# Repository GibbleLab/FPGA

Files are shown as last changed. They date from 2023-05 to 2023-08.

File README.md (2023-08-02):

# Many-Channel FPGA Control System

Authors:
Daniel Schussheim and Kurt Gibble (GibbleLab@psu.edu)

Department of Physics

The Pennsylvania State University

This FPGA system is a general-purpose control system with fast and slow analog inputs and outputs and digital inputs and outputs. The baseline configuration implements 9 PID servos with MHz bandwidths and 8 low bandwidth servos, generates 3 arbitrary waveform outputs, and has modulation, lock-in detection, and digital signal processing.  It was developed to frequency stabilize lasers and frequency doubling and summing cavities, stabilize temperatures, and perform a number of controls and signal processing for a cadmium laser-cooling experiment. The developed hardware and firmware for the inputs and outputs can be used for a variety of applications, connecting the system’s inputs and outputs to the provided or user-developed software filters.

The system uses an Enclustra Mercury+ KX2 FPGA module that plugs into a custom baseboard. The Xilinx FPGA is a XC7K160T-2FFG676I, which has 25,350 logic slices, 600 DSP slices and 325 36 kb RAM blocks. Our baseline FPGA software uses 88,576 look up tables distributed over nearly all, 25,196, of the logic slices. Other pin-compatible FPGA modules with more resources are available. The baseboard was designed with Altium Designer Version 21.3.2 (Build 30), and the power supply board was designed in CircuitMaker.

This work builds on a system developed by [NIST](https://github.com/nist-ionstorage/digital-servo), adding more I/O channels, using a larger FPGA, and simplifying filters to allow more servos on a single FPGA. The software is written in Verilog and the bitstreams were generated with Vivado 2020.1.

The supporting files for this many-channel FPGA system (MCFS) are:

* __manual.pdf__: User guide describing the firmware and software, hardware, and assembly of this MCFS.
* __Mercury_AD_Baseboard__: Altium project with the baseboard design files, gerber and drill files (gerber-drill.rar) for printing, and the bill-of-materials (BOM.xlsx) for assembly.
* __Power_Supply__: The power supply board schematics, board layout, gerber and drill files, and bill-of-materials.
* __MCFS_HD__: Vivado Hierarchical Design Project with the Verilog HDL firmware and software and Tcl scripts for generating bitstreams.
* __Serial-parameter-input__: Spreadsheets to adjust the fast and slow servo gains and roll-off frequencies, arbitrary waveform parameters, and to test the fast DAC’s. A Labview program and its executable file are also included.
* __Vivado GUI Projects__: This [page](https://sites.psu.edu/gibble/fpga_gui) has Vivado GUI projects with simplified PID filters that retain 25% gain resolution with combinations of omitting the LSB rounding of the filter cutoff frequencies or have 2<sup>n</sup> resolution on cutoff frequencies for the proportional or integral filters, or 2<sup>n/2</sup> resolution for the differential rolloff with a damping resolution of 2<sup>n</sup>. These allow timing margin in the full project at 100 MS/s sample rates.

## Schematic of the baseline MCFS software configuration.

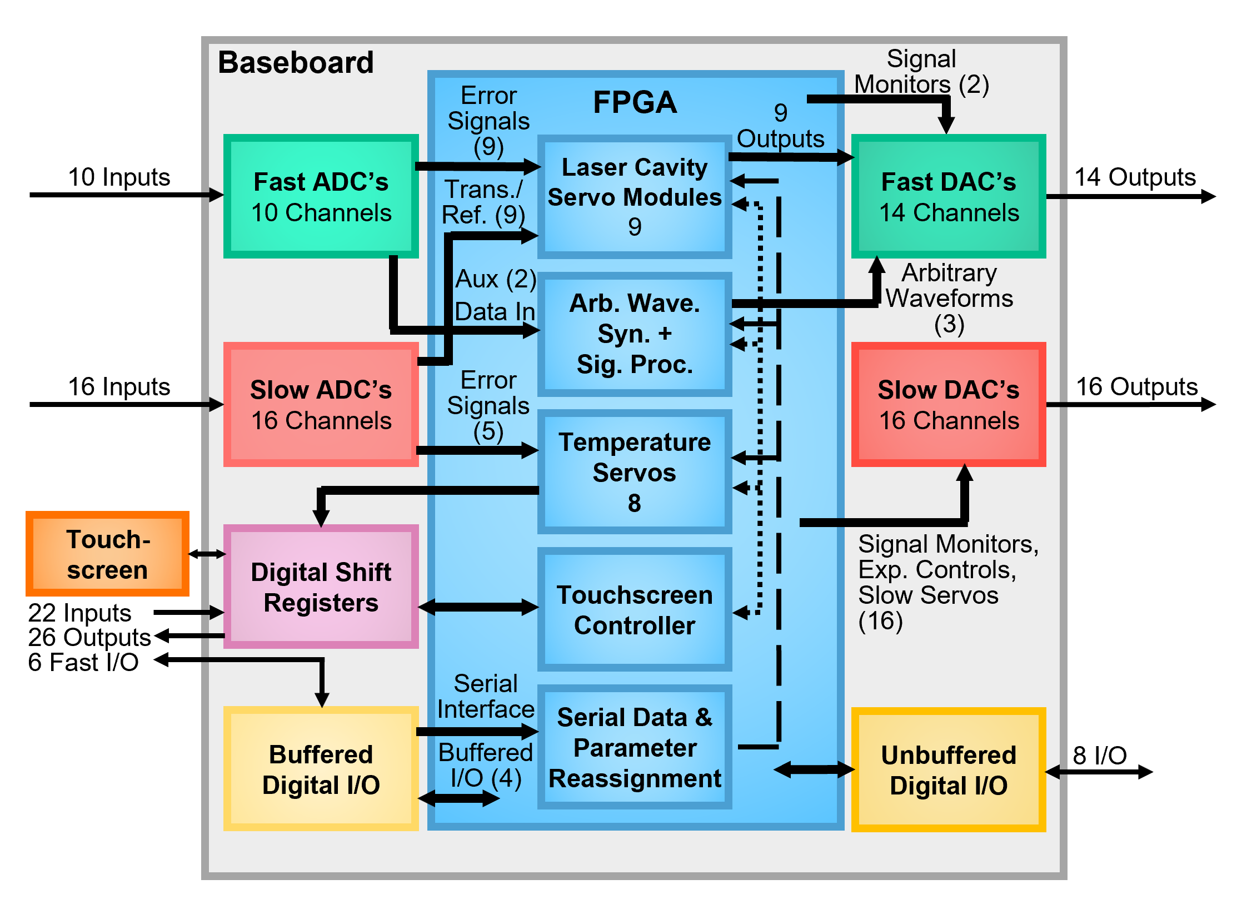
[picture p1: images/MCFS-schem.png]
Schematic


## Summary of inputs and outputs

| I/O Type              |      | # of Channels | Sample Rate (MS/s) | Range (V) |
| :---                  | :--- | :---         | :---               | :---      |
| Fast ADC (LTC2194)    | IN   | 10            | 100                | &#xB1;4   |
| Fast DAC (MAX5875)    | OUT  | 14            | 100                | &#xB1;18  |
| Slow ADC (LTC2335-16) | IN   | 16            | Maximum sample rate is 1 channel every &#x3BC;s on each of 2 chips, e.g., 2 ch. @ 1 MS/s or 16 ch. @ 125 kS/s | &#xB1;10 |
| Slow DAC (LTC2666-16) | OUT  | 16 | 0.05 | &#xB1;18  |
| Fast Digital I/O, buffered (TXS0108E-Q1) | IN/OUT | 6             | 100       | 5V digital |
| Fast Digital I/O, unbuffered (FPC connector) | IN/OUT | 8         | 100+      | 3.3V digital |
| Slow Digital In (74LV165A)  | IN  | 22 | 2 | 3.3V digital |
| Slow Digital Out (74VHC595) | OUT | 26 | 19 ch. @ 2 MS/s, 7 ch. @ 3 MS/s | 3.3V digital |
| Display connectors (DB9)| N/A | 2 | N/A | N/A |

## Additional Information

A paper describing the IIR PID filters, enhanced Hänsch-Couillaud laser locks with slow offset corrections, variable duty cycle temperature servos, and more information about the system is available at:
"[A many-channel FPGA control system](https://doi.org/10.1063/5.0157330)," Daniel T. Schussheim & Kurt Gibble, Rev Sci Instrum <b>94</b>, 085101 (2023); [arXiv:2307.16008](https://arxiv.org/abs/2307.16008).

## Acknowledgements

Financial support to develop this project from the National Science Foundation is gratefully acknowledged.

## License

This work is licensed under a [Creative Commons Attribution-NonCommercial-ShareAlike 3.0 Unported License](https://creativecommons.org/licenses/by-nc-sa/3.0/).

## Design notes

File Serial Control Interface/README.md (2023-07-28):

# Serial Control Interface

The FPGA firmware module serialLine.v uses a two-wire 100 kS/s serial interface to set servo and arbitrary waveform parameters. The serial packet begins and ends with a 16-bit handshake that specifies the parameters to update, which are encoded as 27 sequential 35-bit numbers. 

The gains and other servo parameters, or arbitrary waveform parameters, can be entered into the spreadsheets in this folder. Spreadsheet macros, with keyboard shortcut Ctrl-q, generate the serial packets, writes them to a file param.txt, and calculates the PID transfer function, which is displayed.

The LabVIEW vi Write SRS Arb.vi loads PIDparam.txt as a “point” arbitrary waveform on an SRS DS345 via GPIB. Write SRS Arb.exe is also provided, which requires the 64-bit 2023.Q1 LabVIEW Run-Time Engine. A driver for the GPIB interface may be required; if using the NI GPIB-USB-HS adapter, the 2022 Q4 NI-488.2 driver and NI-488.2 Runtime are needed. For the default firmware, the SRS output should be connected to FPGA pin C12 (serial_in in top.sv) and the SRS trigger output to A14 (serial_trig_in in top.sv). The SRS should be configured for an arbitrary waveform output, with an internal trigger (4 Hz), 100 kHz sample rate, and a 3.2V pk-to-pk amplitude with 0 offset.

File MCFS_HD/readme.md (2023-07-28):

See the manual for the procedure to generate a new bitstream with Vivado HD FLow. The first step is to run Tcl_Script_Generator.tcl, with “source Tcl_Script_Generator.tcl –notrace” in the Vivado 2020.1 Tcl Shell, and then “source MakeBitstream.tcl -notrace”. The design checkpoints, *.dcp, in the Implement and Synth subdirectories /top are for the bitstream, top.bit, which was extensively tested. With 25% resolution on the fast PID rolloff frequencies, it does not have timing margin but nonetheless no operational errors were observed in testing. Some modules have had subsequent minor revisions that are not included in those files. These [GUI Flow projects](https://sites.psu.edu/gibble/fpga_gui), with simplified filter rolloffs, have timing margin.

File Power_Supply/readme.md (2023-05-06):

This is the design for a separate power supply board that uses a single 15 V input to generate the various voltages needed by the baseboard. The source files are available in the CircuitMaker Repository: https://bit.ly/3VuMqpN.

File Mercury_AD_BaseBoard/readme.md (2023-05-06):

Schematic, bill of materials, Gerber and Altium files for the baseboard.

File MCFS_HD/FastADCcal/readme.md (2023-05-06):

See the manual for the procedure to generate bitstreams for Fast ADC testing. After executing Tcl_Script_Generator.tcl in the MCFS_HD directory, the multiphase.tcl and multitap.tcl scripts execute design.tcl multiple times, saving files, including bitstreams and debugging probes files, for each run in Implement\BIT\dump. These are executed in the Vivado 2020.1 Tcl Shell with “source FastADCcal/multiphase.tcl -notrace” and “source FastADCcal/multitap.tcl -notrace”.

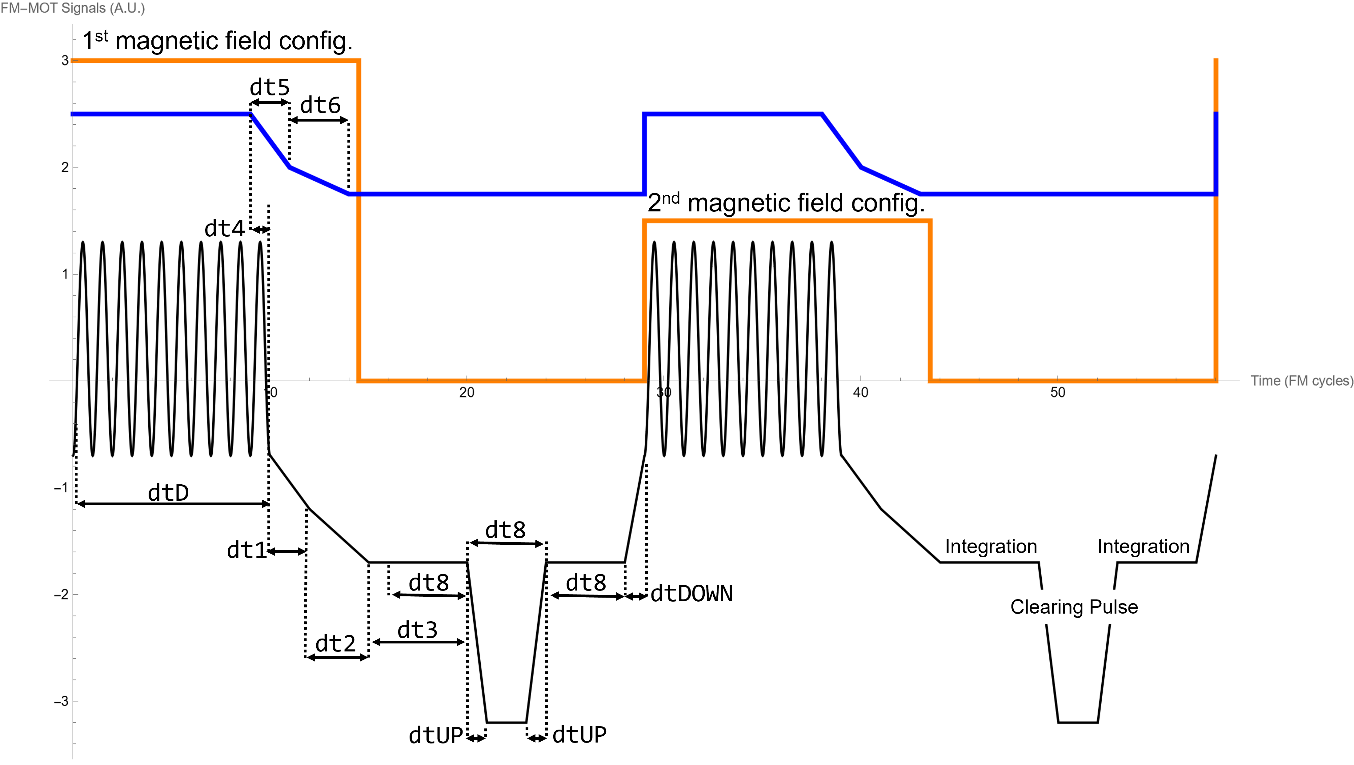
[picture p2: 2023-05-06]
Serial Control Interface/FM-MOT Arbitrary Waveform Definitions.png

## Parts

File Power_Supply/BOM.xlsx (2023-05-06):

Comment | Description | Designator | Quantity
4.7 uF (1210) | CAP CER 4.7UF 50V 10% X7R 1210 | C000, C001, C100, C110, C120, C130, C140, C400 | 8
 | CAP CER 330PF 50V 10% X7R 0603 | C101, C111, C121, C131, C141 | 5
330pF | CAP CER 330PF 50V 10% X7R 0603 | C102, C132, C142 | 3
0.47uF (0805) | Multilayer Ceramic Capacitor, GRM Series, 0.47 F, 10%, X7R, 50 V, 0805 [2012 Metric] | C103, C123, C133, C143 | 4
100pF | CAP CER 330PF 50V 10% X7R 0603 | C104, C107, C114, C117, C124, C127, C134, C137, C144, C147, C200, C203 | 12
0.1uF | CAP CER 330PF 50V 10% X7R 0603 | C105, C108, C115, C118, C125, C128, C135, C138, C145, C148, C201, C204 | 12
22uF, 1210 | CAP CER 22UF 10V 10% X5R 1210 | C106, C109, C136, C139, C146, C149, C202, C205 | 8
680pF | CAP CER 330PF 50V 10% X7R 0603 | C112, C122 | 2
1uF (0805) | Multilayer Ceramic Capacitor, GRM Series, 0.47 F, 10%, X7R, 50 V, 0805 [2012 Metric] | C113 | 1
47uF, 1210 | CAP CER 22UF 10V 10% X5R 1210 | C116, C119, C126, C129 | 4
0.1 uF | Multilayer Ceramic Capacitor, 0.1 F, 10%, X7R, 50 V, 0603 [1608 Metric] | C300, C303, C305, C308, C310, C313, C315, C318, C320, C323, C325, C328, C330, C333, C335, C338, C340, C343, C345, C348, C350, C353, C403 | 23
AVX 22201C106MAT2A | AVX 1μF Multilayer Ceramic Capacitor (MLCC) 100 V dc ±10% X7R Dielectric Standard Series Max. Op. Temp. +125°C | C301, C306, C311, C316, C321, C326, C331, C336, C341, C346, C351 | 11
100 uF | Samsung Electro-Mechanics 100F 20% 10 V X5R Dielectric SMD Ceramic Multilayer Capacitor 1210 | C302, C307, C312, C317, C322, C327, C332, C337, C342, C347, C352 | 11
100 pF | Multilayer Ceramic Capacitor, 0.1 F, 10%, X7R, 50 V, 0603 [1608 Metric] | C304, C309, C314, C319, C324, C329, C334, C339, C344, C349, C354, C402 | 12
0.047 uF | Multilayer Ceramic Capacitor, 0.1 F, 10%, X7R, 50 V, 0603 [1608 Metric] | C401 | 1
2.2 uF (1210) | CAP CER 4.7UF 50V 10% X7R 1210 | C404 | 1
SURS8360BT3G | Surface Mount Ultrafast Power Rectifier, 2-Pin SMB, Pb-Free, Tape and Reel | D000 | 1
MBR0540 | MBR0540 Series 610 mV 500 mA 40 V Max Reverse Voltage Schottky Rectifier-SOD-123 | D100 | 1
MBRM130 | Schottky Power Rectifier, 2-Pin Powermite, Pb-Free, Tape and Reel | D400 | 1
Würth Elektronik 7443551221 | Inductor SMD high current WE-HCI 22uH | L000 | 1
4.7uH (Sumida CDRH8D28NP) | Ind Power Shielded Wirewound 3.3uH 30% 100KHz Ferrite 6A Carrier T/R | L100, L102, L106, L108 | 4
3.3uH (Sumida CDRH8D28NP) | Ind Power Shielded Wirewound 3.3uH 30% 100KHz Ferrite 6A Carrier T/R | L104 | 1
4.7 uH | Ind Power Shielded Wirewound 3.3uH 30% 100KHz Ferrite 6A Carrier T/R | L400 | 1
0 (2512) | Res Thick Film 2512 0.003 Ohm 1% 1W 50ppm/Â°C to 150ppm/Â°C Molded SMD SMD Embossed Carrier T/R | R100, R110, R120, R130, R140, R406, R407, R408, R409 | 9
0 | Res Thick Film 0603 0 Ohm Molded SMD Automotive Punched Paper T/R | R101, R102, R111, R112, R121, R122, R131, R132, R141, R142, R400, R401, R404, R405 | 14
60.4k | Res Thick Film 0603 0 Ohm Molded SMD Automotive Punched Paper T/R | R103, R133, R143 | 3
20k | Res Thick Film 0603 0 Ohm Molded SMD Automotive Punched Paper T/R | R104, R144 | 2
324K | Res Thick Film 0603 0 Ohm Molded SMD Automotive Punched Paper T/R | R105 | 1
200K | Res Thick Film 0603 0 Ohm Molded SMD Automotive Punched Paper T/R | R106, R116, R126, R146 | 4
SHORT | Res Thick Film 0603 0 Ohm Molded SMD Automotive Punched Paper T/R | R107, R108, R117, R118, R127, R128, R137, R138, R147, R148 | 10
SHORT | RC Series 0805 0.125 W 0 O Jumper Surface Mount Thick Film Chip Resistor | R109, R119, R129, R139, R149, R302, R303, R304, R305, R306, R307, R308, R309, R310, R311, R312, R313, R314, R315, R316, R317, R318, R319, R320, R321, R322, R323, R324, R325, R326, R327, R328, R329, R340, R341, R342, R343, R344, R345, R346, R347, R348, R349, R350, R351, R352, R353 | 47
88.7K | Res Thick Film 0603 0 Ohm Molded SMD Automotive Punched Paper T/R | R113, R123 | 2
22k | Res Thick Film 0603 0 Ohm Molded SMD Automotive Punched Paper T/R | R114, R124 | 2
196k | Res Thick Film 0603 0 Ohm Molded SMD Automotive Punched Paper T/R | R115 | 1
84.5k | Res Thick Film 0603 0 Ohm Molded SMD Automotive Punched Paper T/R | R125 | 1
8.66k | Res Thick Film 0603 0 Ohm Molded SMD Automotive Punched Paper T/R | R134 | 1
1M | Res Thick Film 0603 0 Ohm Molded SMD Automotive Punched Paper T/R | R135 | 1
91k | Res Thick Film 0603 0 Ohm Molded SMD Automotive Punched Paper T/R | R136 | 1
590K | Res Thick Film 0603 0 Ohm Molded SMD Automotive Punched Paper T/R | R145 | 1
0 | RES SMD 0.0 OHM JUMPER 1/10W | R200 | 1
600 | RES SMD 0.0 OHM JUMPER 1/10W | R201 | 1
0, 1210 | Thick Film Resistors - SMD 3/4watt ZERO ohm Jumper | R202, R203, R204 | 3
75 | PANASONIC ERJT14J5R6U RESISTOR, ANTI PULSE, 1210, 5R6, 5% | R300, R301 | 2
158k | Res Thick Film 0603 0 Ohm Molded SMD Automotive Punched Paper T/R | R402 | 1
10k | Res Thick Film 0603 0 Ohm Molded SMD Automotive Punched Paper T/R | R403 | 1
LT3681EDE#PBF | 2 A, 2.8 MHz Step-Down Switching Regulator with Integrated Power Schottky Diode, 14-pin SON (DE14MA-14), -40 to 85 degC, Pb-Free | U100, U101, U102, U103, U104 | 5
i6A Series – 1/16th brick Power Module | i6A Series – 1/16th brick Power Module | U200 | 1
MC7805 | Linear Voltage Regulator, Positive, 5.0 V, 1.0 A Vout: 5.0 V; TJ = 0°C to +125°C | U300 | 1
SYM-bdb474be705a6273-1 | Linear Voltage Regulator, Positive, 15 V, 1.0 A Vout: 15.0 V; TJ = 0°C to +125°C | U301, U302, U303, U304 | 4
MC7915 | Linear Voltage Regulator, Negative, 5.0 V, 1.0 A Vout: -15 V; 4%; TJ = 0°C to +125°C | U305, U306 | 2
MC7918 | Linear Voltage Regulator, Negative, 5.0 V, 1.0 A Vout: -15 V; 4%; TJ = 0°C to +125°C | U307, U308 | 2
LT1086 | 1.5 A Low Dropout Positive Regulator, 2.55 to 25 V Vin, Adjustable Vout, 3-pin FM (T-3), -40 to 150 degC, Pb-Free | U309 | 1
MIC39300C | Linear Voltage Regulator, Positive, 15 V, 1.0 A Vout: 15.0 V; TJ = 0°C to +125°C | U310 | 1
LT3467A | 1.1 A Step-Up DC/DC Converter with Integrated Soft-Start MAX, 6-pin SOT23 (S6-6), -40 to 85 degC, Pb-Free, Mini Tape and Reel | U400 | 1

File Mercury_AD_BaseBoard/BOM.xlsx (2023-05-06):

Comment | Description | Designator | Footprint | LibRef | Quantity
15pF |  | C00a0, C00a1, C00a2, C00a3, C00a4, C01a0, C01a1, C01a2, C01a3, C01a4, C04a0, C04a1, C04a2, C04a3, C04a4, C05a0, C05a1, C05a2, C05a3, C05a4, C36a0, C36a1, C36a2, C36a3, C36a4, C37a0, C37a1, C37a2, C37a3, C37a4, C38a0, C38a1, C38a2, C38a3, C38a4, C39a0, C39a1, C39a2, C39a3, C39a4 | 0603 | CAP | 40
0.1uF |  | C00b0, C00b1, C00b2, C00b3, C00b4, C00b5, C00b6, C01b0, C01b1, C01b2, C01b3, C01b4, C01b5, C01b6, C02b0, C02b1, C02b2, C02b3, C02b4, C02b5, C02b6, C03b0, C03b1, C03b2, C03b3, C03b4, C03b5, C03b6, C04b0, C04b1, C04b2, C04b3, C04b4, C04b5, C04b6, C05b0, C05b1, C05b2, C05b3, C05b4, C05b5, C05b6, C06b0, C06b1, C06b2, C06b3, C06b4, C06b5, C06b6, C07b0, C07b1, C07b2, C07b3, C07b4, C07b5, C07b6, C08b0, C08b1, C08b2, C08b3, C08b4, C08b5, C08b6, C10b0, C10b1, C10b2, C10b3, C10b4, C10b5, C10b6, C11b0, C11b1, C11b2, C11b3, C11b4, C11b5, C11b6, C18a0, C18a1, C18a2, C18a3, C18a4, C19a0, C19a1, C19a2, C19a3, C19a4, C20a0, C20a1, C20a2, C20a3, C20a4, C21a0, C21a1, C21a2, C21a3, C21a4, C28a0, C28a1, C28a2, C28a3, C28a4, C29a0, C29a1, C29a2, C29a3, C29a4, C30a0, C30a1, C30a2, C30a3, C30a4, C31a0, C31a1, C31a2, C31a3, C31a4, C32a0, C32a1, C32a2, C32a3, C32a4, C33a0, C33a1, C33a2, C33a3, C33a4, C34a0, C34a1, C34a2, C34a3, C34a4, C35a0, C35a1, C35a2, C35a3, C35a4 | 0402 | CAP | 137
0.1uF |  | C00c0, C00c1, C00d0, C00d1, C01d0, C01d1, C02a0, C02a1, C02a2, C02a3, C02a4, C02c0, C02c1, C02d0, C02d1, C02f, C03a0, C03a1, C03a2, C03a3, C03a4, C03c0, C03c1, C03d0, C03d1, C03f, C04c0, C04c1, C04d0, C04d1, C04f, C05d0, C05d1, C05f, C06a0, C06a1, C06a2, C06a3, C06a4, C06d0, C06d1, C06f, C07a0, C07a1, C07a2, C07a3, C07a4, C07d0, C07d1, C07e, C07f, C08c0, C08c1, C08f, C09d0, C09d1, C09f, C10a0, C10a1, C10a2, C10a3, C10a4, C10d0, C10d1, C10f, C11f, C12e, C12f, C13f, C14f, C15a0, C15a1, C15a2, C15a3, C15a4, C15d0, C15d1, C15f, C16d0, C16d1, C16e, C16f, C17c0, C17c1, C17e, C17f, C18c0, C18c1, C18e, C18f, C19b0, C19b1, C19b2, C19b3, C19b4, C19b5, C19b6, C19e, C20b0, C20b1, C20b2, C20b3, C20b4, C20b5, C20b6, C20e, C21b0, C21b1, C21b2, C21b3, C21b4, C21b5, C21b6, C21d0, C21d1, C21e, C22b0, C22b1, C22b2, C22b3, C22b4, C22b5, C22b6, C22d0, C22d1, C22e, C23e, C24e, C25a0, C25a1, C25a2, C25a3, C25a4, C25e, C26e, C27a0, C27a1, C27a2, C27a3, C27a4, C27c0, C27c1, C27d0, C27d1, C27e, C28c0, C28c1, C28d0, C28d1, C28e, C29b0, C29b1, C29b2, C29b3, C29b4, C29b5, C29b6, C29c0, C29c1, C29e, C31b0, C31b1, C31b2, C31b3, C31b4, C31b5, C31b6, C31c0, C31c1, C33b0, C33b1, C33b2, C33b3, C33b4, C33b5, C33b6, C33c0, C33c1, C33d0, C33d1, C34d0, C34d1, C35b0, C35b1, C35b2, C35b3, C35b4, C35b5, C35b6, C35c0, C35c1, C37c0, C37c1, C39d0, C39d1, C40a0, C40a1, C40a2, C40a3, C40a4, C40d0, C40d1, C42a0, C42a1, C42a2, C42a3, C42a4, C44a0, C44a1, C44a2, C44a3, C44a4, C45d0, C45d1, C46a0, C46a1, C46a2, C46a3, C46a4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 | 0603 | CAP | 235
1uF |  | C00e, C01e, C02e, C04e, C09b0, C09b1, C09b2, C09b3, C09b4, C09b5, C09b6 | 0603 | CAP | 11
100uF |  | C00f, C01f | 1206 | CAP | 2
2.2uF |  | C01c0, C01c1 | 0603 | CAP | 2
10nF |  | C03e, C05e | 0603 | CAP | 2
OPT |  | C05c0, C05c1, C30e, C31e, C32e, C33e, C34e, C35e, C39c0, C39c1, C40c0, C40c1, C41c0, C41c1, C42c0, C42c1, C43c0, C43c1, C44c0, C44c1, C45c0, C45c1, C46c0, C46c1, C47c0, C47c1, C48c0, C48c1, C49c0, C49c1, C50c0, C50c1, C51c0, C51c1, C52c0, C52c1, C53c0, C53c1, C54c0, C54c1, R06e, R07e, R08e, R09e, R10e, R11e | 0603 | CAP, RES | 46
47uF |  | C06c0, C06c1 | 1210 | CAP | 2
0.1 uF |  | C06e, C13e | 0805 | CAP | 2
10uF |  | C07c0, C07c1 | 0805 | CAP | 2
1.8pF |  | C08a0, C08a1, C08a2, C08a3, C08a4, C09a0, C09a1, C09a2, C09a3, C09a4, C13a0, C13a1, C13a2, C13a3, C13a4, C14a0, C14a1, C14a2, C14a3, C14a4 | 0603 | CAP | 20
180pF |  | C08d0, C08d1, C14d0, C14d1, C20d0, C20d1, C26d0, C26d1, C32d0, C32d1, C38d0, C38d1, C44d0, C44d1, C50d0, C50d1 | 0603 | CAP | 16
100pF |  | C08e, C09c0, C09c1, C10c0, C10c1, C11c0, C11c1, C11e, C12c0, C12c1, C13c0, C13c1, C14c0, C14c1, C15c0, C15c1, C16c0, C16c1, C19c0, C19c1, C20c0, C20c1, C21c0, C21c1, C22c0, C22c1, C23c0, C23c1, C24c0, C24c1, C25c0, C25c1, C26c0, C26c1, C30b0, C30b1, C30b2, C30b3, C30b4, C30b5, C30b6, C30c0, C30c1, C32b0, C32b1, C32b2, C32b3, C32b4, C32b5, C32b6, C32c0, C32c1, C34b0, C34b1, C34b2, C34b3, C34b4, C34b5, C34b6, C34c0, C34c1, C36b0, C36b1, C36b2, C36b3, C36b4, C36b5, C36b6, C36c0, C36c1, C38c0, C38c1, C41a0, C41a1, C41a2, C41a3, C41a4, C43a0, C43a1, C43a2, C43a3, C43a4, C45a0, C45a1, C45a2, C45a3, C45a4, C47a0, C47a1, C47a2, C47a3, C47a4, C57d0, C57d1, C59c0, C59c1, C61d0, C61d1, C63d0, C63d1, C65c0, C65c1 | 0603 | CAP | 102
10pF |  | C09e, C10e | 0603 | CAP | 2
300pF |  | C11a0, C11a1, C11a2, C11a3, C11a4, C12a0, C12a1, C12a2, C12a3, C12a4, C16a0, C16a1, C16a2, C16a3, C16a4, C17a0, C17a1, C17a2, C17a3, C17a4 | 0603 | CAP | 20
3.6 nF |  | C11d0, C11d1, C17d0, C17d1, C23d0, C23d1, C29d0, C29d1, C35d0, C35d1, C41d0, C41d1, C47d0, C47d1, C53d0, C53d1 | 0603 | CAP | 16
1uF |  | C12b0, C12b1, C12b2, C12b3, C12b4, C12b5, C12b6 | 0402 | CAP | 7
6.2 nF |  | C12d0, C12d1, C18d0, C18d1, C24d0, C24d1, C30d0, C30d1, C36d0, C36d1, C42d0, C42d1, C48d0, C48d1, C54d0, C54d1 | 0603 | CAP | 16
100 pF |  | C13b0, C13b1, C13b2, C13b3, C13b4, C13b5, C13b6, C15b0, C15b1, C15b2, C15b3, C15b4, C15b5, C15b6, C16b0, C16b1, C16b2, C16b3, C16b4, C16b5, C16b6, C18b0, C18b1, C18b2, C18b3, C18b4, C18b5, C18b6 | 0603 | CAP | 28
10 nF |  | C13d0, C13d1, C19d0, C19d1, C25d0, C25d1, C31d0, C31d1, C37d0, C37d1, C43d0, C43d1, C49d0, C49d1, C55d0, C55d1 | 0603 | CAP | 16
1 nF |  | C14b0, C14b1, C14b2, C14b3, C14b4, C14b5, C14b6, C17b0, C17b1, C17b2, C17b3, C17b4, C17b5, C17b6 | 0603 | CAP | 14
0805interdigitated |  | C22a0, C22a1, C22a2, C22a3, C22a4 | 0805int | 0805intCap | 5
2.2uF |  | C23a0, C23a1, C23a2, C23a3, C23a4 | 0402 | CAP | 5
430 pF |  | C23b0, C23b1, C23b2, C23b3, C23b4, C23b5, C23b6, C26b0, C26b1, C26b2, C26b3, C26b4, C26b5, C26b6 | 0603 | CAP | 14
10uF |  | C24a0, C24a1, C24a2, C24a3, C24a4, C26a0, C26a1, C26a2, C26a3, C26a4 | 0603 | CAP | 10
1100 pF |  | C24b0, C24b1, C24b2, C24b3, C24b4, C24b5, C24b6, C27b0, C27b1, C27b2, C27b3, C27b4, C27b5, C27b6 | 0603 | CAP | 14
1000 pF |  | C25b0, C25b1, C25b2, C25b3, C25b4, C25b5, C25b6, C28b0, C28b1, C28b2, C28b3, C28b4, C28b5, C28b6 | 0603 | CAP | 14
IP4285CZ6-TD |  | D0e, D1e | 6-TSOP | IP4285CZ6-TD | 2
MBR0530 |  | D2e, D3e | SOD123 | Schottky_Diode | 2
302-S101 | JTAG Connector | J0e | 3020-10-0300-00 | JTAG_10 | 1
FX10A-168P-SV(71) | Mercury Baseboard Connector | J0f, J1f, J2f | Mercury_Baseboard_Connector | Mercury_Baseboard_Connector-A, Mercury_Baseboard_Connector-B, Mercury_Baseboard_Connector-C | 3
87583-3010RPALF |  | J1e | 87583-3010RPALF | 87583-3010RPALF | 1
L829-1J1T-43 |  | J2e | L829-1J1T-43 | L829-1J1T-43 | 1
1-1734592-2 |  | J3f | FPC12 | FPC12 | 1
DB9 |  | J4e, J5e | 9-Pin_D-Connector_SMT | DB9 | 2
180-M44-113R911 |  | J6e | 180-M44-213R911 | DSUB44 | 1
fADC GND pads |  | Ja0, Ja1, Ja2, Ja3 | FADC_GND_CONN | fADC GND pads | 4
fDAC GND pads |  | Jb0, Jb1, Jb2, Jb3, Jb4 | fDAC_GND_conn | fADC GND pads | 5
0603 bead |  | L00a0, L00a1, L00a2, L00a3, L00a4, L00b0, L00b1, L00b2, L00b3, L00b4, L00b5, L00b6, L00c0, L0c1, L0e, L01a0, L01a1, L01a2, L01a3, L01a4, L01b0, L01b1, L01b2, L01b3, L01b4, L01b5, L01b6, L01c0, L1c1, L1e, L02a0, L02a1, L02a2, L02a3, L02a4, L02b0, L02b1, L02b2, L02b3, L02b4, L02b5, L02b6, L02c0, L2c1, L03a0, L03a1, L03a2, L03a3, L03a4, L03b0, L03b1, L03b2, L03b3, L03b4, L03b5, L03b6, L03c0, L3c1, L04b0, L04c0, L4c1, L05a0, L05a1, L05a2, L05a3, L05a4, L05c0, L5c1, L06a0, L06a1, L06a2, L06a3, L06a4, L06b0, L07b0, L07c0, L07c1, L08a0, L08a1, L08a2, L08a3, L08a4, L08b0, L08b1, L08b2, L08b3, L08b4, L08b5, L08b6, L08c0, L08c1, L09a0, L09a1, L09a2, L09a3, L09a4, L09b0, L09c0, L09c1, L10a0, L10a1, L10a2, L10a3, L10a4, L10b0, L10b1, L10b2, L10b3, L10b4, L10b5, L10b6, L10c0, L10c1, L11a0, L11a1, L11a2, L11a3, L11a4, L11b0, L11b1, L11b2, L11b3, L11b4, L11b5, L11b6, L11c0, L11c1, L12b0, L12b1, L12b2, L12b3, L12b4, L12b5, L12b6, L12c0, L12c1, L13b0, L13b1, L13b2, L13b3, L13b4, L13b5, L13b6, L13c0, L13c1, L14b1, L14b2, L14b3, L14b4, L14b5, L14b6, L14c0, L14c1, L15b1, L15b2, L15b3, L15b4, L15b5, L15b6, L15c0, L15c1, L16b1, L16b2, L16b3, L16b4, L16b5, L16b6, L16c0, L16c1, L16d0, L16d1, L17b1, L17b2, L17b3, L17b4, L17b5, L17b6, L17c0, L17c1, L17d0, L17d1, L18c0, L18c1, L19c0, L19c1, L19d0, L19d1, L20c0, L20c1, L20d0, L20d1, L21c0, L21c1, L21d0, L21d1, L22c0, L22c1, L22d0, L22d1, L23c0, L23c1, L23d0, L23d1 | 0603 | INDUCTOR | 203
Ltotal = 500 uH | 5x 100 uH + 1 short | L00d0, L00d1, L01d0, L01d1, L02d0, L02d1, L03d0, L03d1, L04d0, L04d1, L05d0, L05d1, L06d0, L06d1, L07d0, L07d1, L08d0, L08d1, L09d0, L09d1, L10d0, L10d1, L11d0, L11d1, L12d0, L12d1, L13d0, L13d1, L14d0, L14d1, L15d0, L15d1 | SMT_TOROID_2SIDE | SMT_TOROID_2SIDE | 32
1uH |  | L00f, L01f | 1206 | INDUCTOR | 2
1206 bead |  | L04a0, L04a1, L04a2, L04a3, L04a4, L05b0, L06c0, L6c1, L07a0, L07a1, L07a2, L07a3, L07a4, L09b1, L09b2, L09b3, L09b4, L09b5, L09b6, L18d0, L18d1 | 1206 | INDUCTOR | 21
2.2 uH |  | L4b0, L04b1, L04b2, L04b3, L04b4, L04b5, L04b6, L6b0, L06b1, L06b2, L06b3, L06b4, L06b5, L06b6 | 0603 | INDUCTOR | 14
2.7 uH |  | L5b0, L05b1, L05b2, L05b3, L05b4, L05b5, L05b6, L7b0, L07b1, L07b2, L07b3, L07b4, L07b5, L07b6 | 0603 | INDUCTOR | 14
1k |  | R00a0, R00a1, R00a2, R00a3, R00a4, R00f, R01a0, R01a1, R01a2, R01a3, R01a4, R02a0, R02a1, R02a2, R02a3, R02a4, R03a0, R03a1, R03a2, R03a3, R03a4, R06a0, R06a1, R06a2, R06a3, R06a4, R07a0, R07a1, R07a2, R07a3, R07a4, R08a0, R08a1, R08a2, R08a3, R08a4, R09a0, R09a1, R09a2, R09a3, R09a4, R11d0, R11d1 | 0603 | RES | 43
100 |  | R0a, R31a0, R31a1, R31a2, R31a3, R31a4 | 0402 | RES | 6
33 |  | R00b0, R00b1, R00b2, R00b3, R00b4, R00b5, R00b6 | 0402 | RES | 7
10k |  | R00c0, R00c1, R01c0, R01c1, R03c0, R03c1, R04c0, R04c1, R05c0, R05c1, R06c0, R06c1, R08c0, R08c1, R09c0, R09c1, R10c0, R10c1, R11c0, R11c1, R12d0, R12d1, R13c0, R13c1, R13d0, R13d1, R14c0, R14c1, R15c0, R15c1, R16c0, R16c1, R16d0, R16d1, R17d0, R17d1, R18c0, R18c1, R19c0, R19c1, R20c0, R20c1, R20d0, R20d1, R21c0, R21c1, R21d0, R21d1, R23c0, R23c1, R24c0, R24c1, R24d0, R24d1, R25c0, R25c1, R25d0, R25d1, R26c0, R26c1, R28c0, R28c1, R28d0, R28d1, R29c0, R29c1, R29d0, R29d1, R30c0, R30c1, R31c0, R31c1, R32d0, R32d1, R33c0, R33c1, R33d0, R33d1, R34c0, R34c1, R35c0, R35c1, R36c0, R36c1, R36d0, R36d1, R37d0, R37d1, R38c0, R38c1, R39c0, R39c1, R40c0, R40c1, R40d0, R40d1, R41d0, R41d1 | 0603 | RES | 98
SHORT |  | R00d0, R00d1, R01d0, R01d1, R02b0, R02b1, R02b2, R02b3, R02b4, R02b5, R02b6, R02d0, R02d1, R03b0, R03b1, R03b2, R03b3, R03b4, R03b5, R03b6, R04b0, R04b1, R04b2, R04b3, R04b4, R04b5, R04b6, R05b0, R05b1, R05b2, R05b3, R05b4, R05b5, R05b6, R05e, R06b0, R06b1, R06b2, R06b3, R06b4, R06b5, R06b6, R28a0, R28a1, R28a2, R28a3, R28a4, R29a0, R29a1, R29a2, R29a3, R29a4, R44d0, R44d1, R45d0, R45d1, R46d0, R46d1, R47d0, R47d1, R48d0, R48d1, R49d0, R49d1 | 0603 | RES | 64
22 |  | R00e, R01e, R02e, R03e | 0603 | RES | 4
1.91k |  | R01b0, R01b1, R01b2, R01b3, R01b4, R01b5, R01b6 | 0603 | RES | 7
49.9 |  | R02c0, R02c1, R03d0, R03d1, R04d0, R04d1, R05a0, R05a1, R05a2, R05a3, R05a4, R05d0, R05d1, R06d0, R06d1, R07c0, R07c1, R07d0, R07d1, R08b0, R08b1, R08b2, R08b3, R08b4, R08b5, R08b6, R08d0, R08d1, R09d0, R09d1, R10d0, R10d1, R11a0, R11a1, R11a2, R11a3, R11a4, R11b0, R11b1, R11b2, R11b3, R11b4, R11b5, R11b6, R12c0, R12c1, R17c0, R17c1, R18a0, R18a1, R18a2, R18a3, R18a4, R19a0, R19a1, R19a2, R19a3, R19a4, R19b0, R19b1, R19b2, R19b3, R19b4, R19b5, R19b6, R20b0, R20b1, R20b2, R20b3, R20b4, R20b5, R20b6, R22c0, R22c1, R26a0, R26a1, R26a2, R26a3, R26a4, R27a0, R27a1, R27a2, R27a3, R27a4, R27c0, R27c1, R32c0, R32c1, R37c0, R37c1 | 0603 | RES | 90
150 |  | R04a0, R04a1, R04a2, R04a3, R04a4, R10a0, R10a1, R10a2, R10a3, R10a4 | 0603 | RES | 10
600 |  | R04e | 0603 | RES | 1
25 |  | R07b0, R07b1, R07b2, R07b3, R07b4, R07b5, R07b6, R09b0, R09b1, R09b2, R09b3, R09b4, R09b5, R09b6, R10b0, R10b1, R10b2, R10b3, R10b4, R10b5, R10b6, R12b0, R12b1, R12b2, R12b3, R12b4, R12b5, R12b6 | 0603 | RES | 28
220 |  | R12a0, R12a1, R12a2, R12a3, R12a4, R13a0, R13a1, R13a2, R13a3, R13a4, R20a0, R20a1, R20a2, R20a3, R20a4, R21a0, R21a1, R21a2, R21a3, R21a4 | 0603 | RES | 20
33 |  | R13b0, R13b1, R13b2, R13b3, R13b4, R13b5, R13b6, R14b0, R14b1, R14b2, R14b3, R14b4, R14b5, R14b6, R15b0, R15b1, R15b2, R15b3, R15b4, R15b5, R15b6, R16b0, R16b1, R16b2, R16b3, R16b4, R16b5, R16b6 | 0603 | RES | 28
249 |  | R14a0, R14a1, R14a2, R14a3, R14a4, R15a0, R15a1, R15a2, R15a3, R15a4, R22a0, R22a1, R22a2, R22a3, R22a4, R23a0, R23a1, R23a2, R23a3, R23a4 | 0603 | RES | 20
18k |  | R14d0, R14d1, R18d0, R18d1, R22d0, R22d1, R26d0, R26d1, R30d0, R30d1, R34d0, R34d1, R38d0, R38d1, R42d0, R42d1 | 0603 | RES | 16
400 |  | R15d0, R15d1, R19d0, R19d1, R23d0, R23d1, R27d0, R27d1, R31d0, R31d1, R35d0, R35d1, R39d0, R39d1, R43d0, R43d1 | 0603 | RES | 16
75 |  | R16a0, R16a1, R16a2, R16a3, R16a4, R17a0, R17a1, R17a2, R17a3, R17a4, R24a0, R24a1, R24a2, R24a3, R24a4, R25a0, R25a1, R25a2, R25a3, R25a4 | 0603 | RES | 20
140 |  | R17b0, R17b1, R17b2, R17b3, R17b4, R17b5, R17b6, R18b0, R18b1, R18b2, R18b3, R18b4, R18b5, R18b6 | 0402 | RES | 14
1 |  | R21b0, R21b1, R21b2, R21b3, R21b4, R21b5, R21b6, R41c0, R41c1, R58d0, R58d1 | 0603 | RES | 11
100 |  | R30a0, R30a1, R30a2, R30a3, R30a4 | 0603 | RES | 5
185 |  | R50d0, R50d1, R51d0, R51d1, R52d0, R52d1, R53d0, R53d1, R54d0, R54d1, R55d0, R55d1, R56d0, R56d1, R57d0, R57d1 | 0603 | RES | 16
2k |  | Ra1 | 0603 | RES | 1
SDA01H1SBD |  | SW0e | SDA01H1SBD | SW1 | 1
OPA228 |  | U0a0, U0a1, U0a2, U0a3, U0a4, U1a0, U1a1, U1a2, U1a3, U1a4 | 8SOIC | LF356 | 10
MAX5875 |  | U0b0, U0b1, U0b2, U0b3, U0b4, U0b5, U0b6 | 68LQFN | MAX5875 | 7
LTC2335-16 |  | U0c0, U0c1 | 48LQFP | LTC2335-16 | 2
LTC2666 |  | U0d0, U0d1 | 32QFN | LTC2666 | 2
LTC6752 |  | U0e | sc70 | LTC6752 | 1
74VHC595 |  | U0f, U1f, U3e, U4e, U5e | 16TSSOP | 74VHC595 | 5
AD8421 |  | U1b0, U1b1, U1b2, U1b3, U1b4, U1b5, U1b6, U2b0, U2b1, U2b2, U2b3, U2b4, U2b5, U2b6 | 8SOIC | AD8421 | 14
LTC6655-4.096 |  | U1c0, U1c1 | 8MSOP_1 | LTC6655 | 2
LF356 |  | U1d0, U1d1, U2d0, U2d1, U3d0, U3d1, U4d0, U4d1, U5d0, U5d1, U6d0, U6d1, U7d0, U7d1, U8d0, U8d1 | 8SOIC | LF356 | 16
TXS0108E-Q1 |  | U1e, U2e, U2f | R-PDSO-G20 | 8BitLevelShifter | 3
LTC6406 |  | U2a0, U2a1, U2a2, U2a3, U2a4, U3a0, U3a1, U3a2, U3a3, U3a4 | 8MSOP | LTC6406 | 10
AD8513 |  | U2c0, U2c1, U3c0, U3c1 | 14TSSOP | OPAMPx4 | 4
ADR127 |  | U4a0, U4a1, U4a2, U4a3, U4a4 | 6TSOT | ADR12x | 5
LTC2194 |  | U5a0, U5a1, U5a2, U5a3, U5a4 | 52QFN | LTC2194 | 5
74LV165A |  | U6e, U7e, U8e | 16TSSOP | 74LV165A | 3

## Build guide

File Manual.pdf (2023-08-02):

1

# User Guide: A Many‐Channel FPGA Control System

## Daniel Schussheim and Kurt Gibble (kgibble@psu.edu)

## Introduction

Here we describe a general‐purpose many‐channel FPGA system (MCFS) that can implement numerous high‐ and low‐speed PID servos, generate arbitrary waveforms, modulate and lock‐in detect and perform digital signal processing.¹ We developed it to frequency lock laser cavities, stabilize temperatures and perform a number of controls and signal processing to laser‐cool cadmium atoms. The system’s inputs and outputs are:

3BTABLE 1: Inputs and Outputs
I/O type | # of channels | Sample rate (MS/s) | Range (V)
Fast ADC (LTC2194) | IN | 10 | 100 | ±4
Fast DAC (MAX5875) | OUT | 14 | 100 | ±18
Slow ADC (LTC2335‐16) | IN | 16 | Maximum sample rate is 1 channel every µs on each of 2 chips, e.g., 2 ch. @ 1 MS/s or 16 ch. @ 125 kS/s | ±10
Slow DAC (LTC2666‐16) | OUT | 16 | 0.05 | ±18
Fast Digital I/O, buffered (TXS0108E‐Q1) | IN/OUT | 6 | 100 | 5V digital
Fast Digital I/O, unbuffered (FPC connector) | IN/OUT | 8 | 100+ | 3.3V digital
Slow Digital In (74LV165A) | IN | 22 | 2 | 3.3V digital Slow Digital Out (74VHC595) | OUT | 26 | 19
7 | 3
Display connectors (DB9) | N/A | 2 | N/A | N/A

This MCFS uses an Enclustra Mercury+ KX2 FPGA module that plugs into the baseboard. The baseboard uses all 216 accessible FPGA input/output (I/O). The Xilinx FPGA part number is XC7K160T‐ 2FFG676I, which has 25,350 logic slices, each containing 4 look‐up tables and 8 flip‐flops; 600 DSP slices, containing a pre‐adder, a 25×18 multiplier, a ternary adder and an accumulator; and 325 36 kb RAM blocks. Our baseline FPGA software uses 88,576 (87.4%) of the look‐up tables distributed over nearly all of the logic slices. Other pin‐compatible FPGA modules with more resources are available.
We use the system to control laser frequencies, optical cavity lengths, and the temperatures of cavities and nonlinear optical crystals. This work builds on a system developed by NIST,² adding more I/O channels, using a larger FPGA, and simplifying some filters to allow more servos on a single FPGA. This

2

user guide describes the hardware, and software and firmware developed for this control system, including generating programming files (bitstreams) for the FPGA.
The software is written in Verilog, bitstreams are generated with a Hierarchical Design Flow with Vivado 2020.1, the baseboard was designed with Altium Designer Version 21.3.2 (Build 30), and the power supply board was designed in CircuitMaker.³

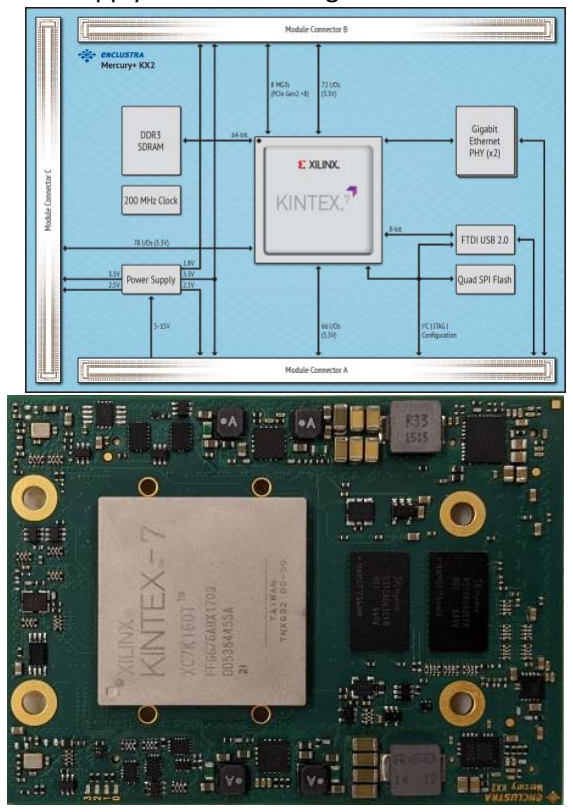
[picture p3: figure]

0BFIG. 1. Enclustra Mercury+ KX2 FPGA module functional diagram (from enclustra.com) and photograph.

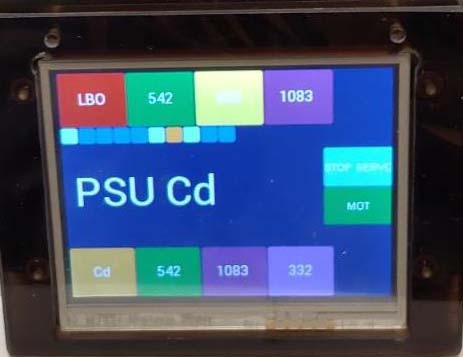
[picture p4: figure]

1BFIG. 2. LCD touch screen display.

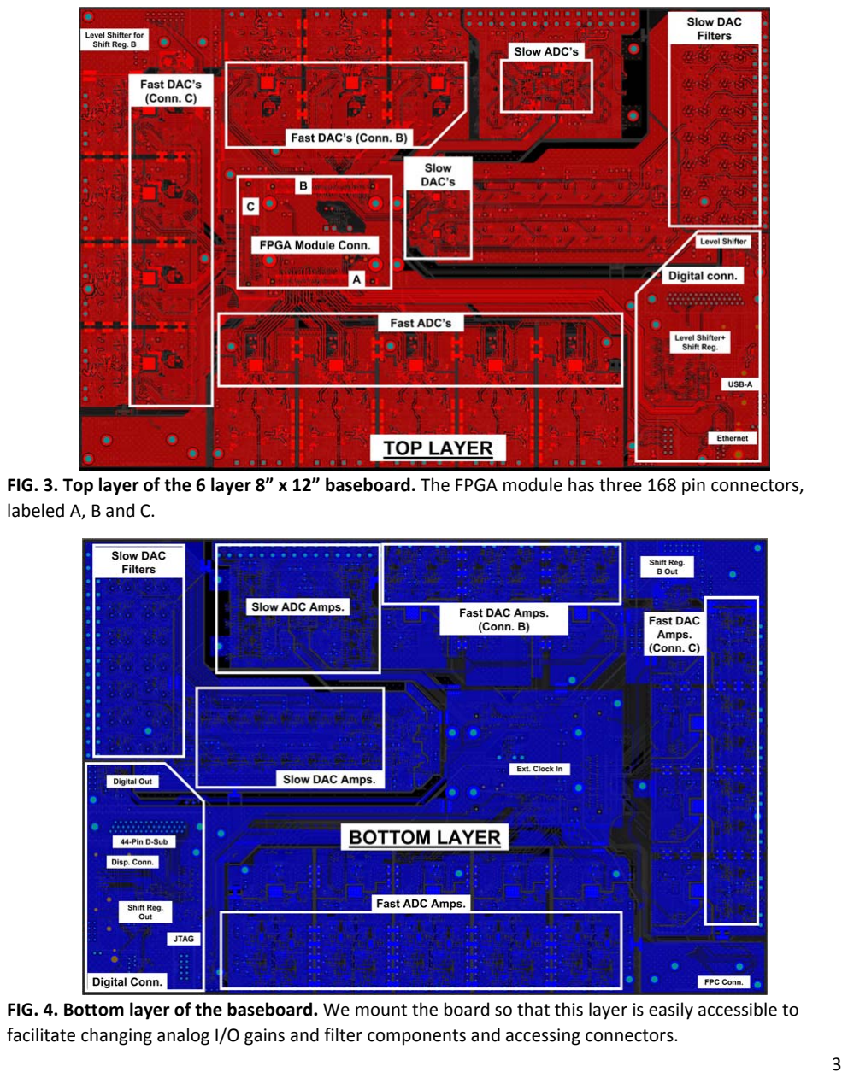
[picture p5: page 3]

3

FIG. 3. Top layer of the 6 layer 8” x 12” baseboard. The FPGA module has three 168 pin connectors, labeled A, B and C.

FIG. 4. Bottom layer of the baseboard. We mount the board so that this layer is easily accessible to facilitate changing analog I/O gains and filter components and accessing connectors.

4

## Contents

Introduction | 1
Hardware | 6
FPGA module | 6
Analog‐to‐digital converters (ADC’s) | 6
Digital‐to‐analog converters (DAC’s) | 6
Digital I/O | 6
External Clock Input | 6
LCD touch screen | 7
Software | 7
Touchscreen LCD Driver: display.v, LCD_header.v and SR_CTRL.v | 11
Firmware | 12
Fast ADC’s: LTC2194.v, LTC2194DDR.v, BitslipDynamic.v and BitslipStatic.v | 15
Calibrating the Fast ADC ISERDESE2 Delays | 15
Fast DAC’s: MAX5875.v | 16
Slow, Multichannel, Serial ADC’s: LTC2335_16.sv | 16
Slow, Multichannel, Serial DAC’s: LTC2666x2.sv | 16
Adjusting Parameters with serialLine.v | 17
Programming the FPGA | 17
Flash Programming | 18
Synthesizing and Implementing Bitstreams | 18
Quick Start Guide and Summary | 18
Hierarchical Design (HD) Flow | 20
Hierarchical Design .prj Files | 20
OOC Module Synthesis | 20
Top‐Down Implementation for OOC Implementation | 21
OOC Implementation | 23
Top Implementation | 23
Debugging Probes | 24
HD Flow Examples to Modify display | 25

5

Fast ADC Calibration Scripts | 26
Suggestions on Debugging HD Flow | 26
Power supply board | 27
Assembly notes | 30
USB, Ethernet, Multi‐Gigabit Transceivers | 31
Acknowledgements | 32
References | 32

6

## Hardware

The following is a list of the main hardware components for the MCFS baseboard. A full component list is available in the bill‐of‐materials, “BOM.xlsx,” in the repository.⁴

### FPGA module

Mercury+ KX2: FPGA module ME‐KX2‐160‐2I‐D11‐P from Enclustra GmbH with an XC7K160T‐2FFG676I FPGA. This module combines a Xilinx Kintex‐7 FPGA with fast DDR3 SDRAM, an FTDI USB 2.0 controller, dual Gigabit Ethernet, multi‐gigabit transceivers, and high‐speed low‐voltage differential signaling (LVDS) I/O. Documentation is available from Enclustra.

### Analog‐to‐digital converters (ADC’s)

LTC2194 (×5): 16‐bit, 2‐channel simultaneous‐sampling ADC, with a 105 MS/s maximum sampling rate and serial LVDS digital outputs. They have a ±4 V range in the default baseboard configuration. LTC2335‐16 (×2): 16‐bit, 8‐channel multiplexed ADC. The channels can be sampled in any order with a specified maximum conversion rate of 1 MS/s. For example, reading channels {1, 2, 1, 3, 1, 5, 1, 6, 1, 7} at 1 MS/s updates channel 1 every 2 μs, channels 2, 3, 5, 6 and 7 every 10 μs, and channels 0 and 4 are never read. The ADC can sample a specified channel on each conversion cycle, or a repeating sequence of up to 16 channels can be programmed. It uses a serial‐peripheral interface (SPI) digital I/O bus. The default configuration is reading the channels in order, {0, 1, 2, 3, 4, 5, 6, 7} with a ±10 V input range.

### Digital‐to‐analog converters (DAC’s)

MAX5875 (×7): 16‐bit, 200 MS/s, dual‐channel, current‐output DAC. The DAC uses a parallel CMOS I/O bus. The MCFS uses the interleaved mode to reduce the number of FPGA I/O used per chip, updating each channel at 100 MS/s. They have a range of ±18 V in the default baseboard configuration. LTC2666‐16 (×2): 16‐bit, 8‐channel multiplexed DAC with a specified maximum update rate of 50 kS/s. The DAC’s are programmed over an SPI bus and channels can be updated in an arbitrary order. They have a ±18 V range in the default baseboard configuration.

### Digital I/O

TXS0108E‐Q1 (×2): 8‐bit bidirectional, level‐shifting, voltage translator, used to buffer FPGA digital I/O. Each chip buffers 8 lines, updating at up to 110 Mb/s (megabits per second).
74LV165A (×3): 8‐bit parallel‐load serial‐in shift register, reading 24 digital inputs at nominally 2 MS/s. 74VHC595 (×5): 8‐bit serial‐in, parallel‐out CMOS shift‐register, driving 24 digital outputs at nominally 2 MS/s. A second bank drives 16 digital outputs at nominally 2.94 MS/s, 50/(16+1) MS/s.

### External Clock Input

LTC6752: High‐speed comparator for an external clock input. This is included on the baseboard but we have not tested or used it. Direct connections on the baseboard for an external digital clock input are also provided.

7

### LCD touch screen

NHD‐3.5‐320240FT‐CTXL‐T: 3.5” LCD module with resistive touch sensing. It uses a FTDI/Bridgetek FT812 Embedded Video Engine (EVE2), supports audio, and has 1 MB of internal graphics RAM, built‐in scalable fonts, 24‐bit color and 320×240 resolution. It is programmed over an SPI bus and supports single‐, dual‐, or quad‐wire modes; the MCFS baseboard is configured for the single‐wire mode.

## Software

Several software modules implement digital filters, dither modulation and lock‐in detection, arbitrary waveform generation, drivers for an LCD touchscreen, and other DSP.¹ The following list describes the software modules for the MCFS, where parent modules instantiate modules listed under them. There is additional discussion of the display control at the end of this section.

Top.sv: The top‐level module that contains all other module instances. It begins with declaring the port names for the signals connected to the FPGA I/O pins, and ultimately to the baseboard. These connections are specified in the constraints file, top.xdc. Five sections follow: SIGNAL DECLARATIONS, SIGNAL ASSIGNMENTS, MODULE DECLARATIONS, FAST DAC TESTING SECTION, and PARAMETER REASSIGNMENT. SIGNAL DECLARATIONS defines the signals used in top.sv and that connect to modules instantiated in it. These may include default values, such as default servo parameters. SIGNAL ASSIGNMENTS defines signal connections, notably high‐level connections of software signals such as a cavity error or servo output to firmware I/O signals, i.e., a particular ADC/DAC channel. Modules are instantiated in MODULE DECLARATIONS: cavity servos; temperature servos; FM‐ MOT modules; display modules; ADC, DAC and shift‐register firmware; serial input firmware; and clocking firmware. The FAST DAC TESTING SECTION has the signal declarations and module instances of Sweep.v and rmp_sml.v, which are used to optimize the fast DAC clock phase and measure their bipolar offset errors. Finally, PARAMETER REASSIGNMENT updates the parameter values received from the serial input module. Here, parameters can be conveniently fixed to a default value by inhibiting reassignment in this section.
Gated_clk.v: Generates low‐frequency clock signal using the 7‐series FPGA primitive, BUFGCE. A counter enables a clock pulse once every cntMAX cycles. For example, to make a 1 MHz clock, cntMAX = 100. This is the recommended architecture for generating low‐frequency clocks that the Vivado design timing tools can interpret as a clock without specifying additional timing constraints. Reset.v: A high EN input enables a counter that generates a 1‐bit output, high from 100 to 200 μs after the counter starts, for a 100 MHz clock input. Just after the bitstream is loaded, the clock manager is reset, and several other modules (FastADCsDDR.v, SlowADCs.sv, TempServos.v, SR_CTRL.v for the display) are reset with a second instance. A third instance allows SR_CTRL.v for the display to be reset, which also reinitializes the display, when a reset signal is sent via the serial input.
Sig1Dly.v: Generates a delayed logic output that is high N clock cycles after a falling trigger. It is used to delay the sleep mode of the fast DAC’s and slow ADC’s after the servos are turned off.

8

CavServos.v: Parent module that instantiates up to 10 fast cavity servos. The servos include a PID filter, auto‐lock, a dither lock correction (a dither lock for servo 5), and overflow and underflow protection.
AutoLock.v: Generates the auto‐lock sweep and enable for the fast cavity servos. It can be configured in several modes: using transmission or reflection as an input, various sweep configurations, and an optional secondary enable, for example to sequentially lock cavity servos. Sweep.v: This module, from NIST,² makes a triangle wave. Two control inputs, on and hold, enable the ramp and hold the current value. A resetmode parameter has been added, which sets the off (on = 0) state output to be zero or its maximum value. ErrorScaleShift.v: Bit‐shifts an error signal and adds an offset and modulation. CavPID.v uses this as an input.
CavPID.v: Implements a fast PID servo, which we use for laser cavity servos.
I1BS.v: A 1st order integral filter with an optional low‐frequency gain cap. The filter is implemented using bit‐shift‐addition operations instead of multipliers, and has a 25% gain and frequency resolution, i.e., the filter coefficients can be: … 0.5, 0.625, 0.75, 0.875 1, 1.25, 1.5, 1.75, 2, .... It has upper and lower output limits, and an input (nominally from the proportional filter output) that is subtracted from the limits, to prevent integrator wind‐up. The module has an adjustable input and output signal size and an adjustable number of internal fractional bits. It allows timing margin at 100 MS/s with 25‐bit input/output words and 32 additional internal fractional bits.
P1BS.v: A 1st order proportional bit‐shift‐addition filter with a high‐frequency roll‐down. The filter has a 25% gain and frequency resolution and upper and lower limits to prevent overflow and underflow. The module has adjustable input and output signal size and an adjustable number of internal fractional bits. It allows timing margin at 100 MS/s with 25‐bit input/output words and 32 additional internal fractional bits.
DBS_rolloff.v: A 2nd order differential bit‐shift‐addition filter with a linewidth and a high‐ frequency roll‐down. It has a 25% gain resolution and the frequency and linewidth coefficients have 2n precision, which gives a resolution of factors of √2 for the high‐ frequency roll‐down, and factors of 2 for the linewidth. Adjustable higher‐precision frequency and linewidth coefficients did not have timing margin at 100 MS/s, but may nonetheless work. The filter has upper and lower limits to prevent overflow and underflow. The module has adjustable input and output signal size and an adjustable number of internal fractional bits. It allows timing margin at 100 MS/s with 25‐bit input and output words and 16 additional internal fractional bits.
CavPID_rolloff.v: A variant of CavPID.v with 2N resolution for the rolloff frequencies to provide more timing margin.
I1BS_rolloff.v and P1BS_rolloff.v: Variants of I1BS.v and P1BS.v, with 2N resolution for the cutoff and rolloff frequencies to provide more timing margin. CavPID_nornd.v: A variant of CavPID.v, with I1BS_rolloff.v and P1BS_nornd.v to provide more timing margin.

9

P1BS_nornd.v, P1BS_nornd.v, and DBS_nornd.v: Variants of P1BS.v, I1BS.v and DBS.v that have more timing margin by omitting the LSB rounding of the rolloff and cutoff frequency and damping contributions to the filter outputs while retaining 25% resolution of the frequency terms.
DitherLock.v: Parent module that instantiates a lock‐in amplifier and modulation waveform generator, with logic to delay the start of the modulation. The demodulated output connects to an integrator (I1BS.v), whose output corrects an error signal, e.g., a Hänsch‐Couillaud error signal, to lock to the maximum of a cavity’s transmission. This module outputs the inhtrig signal that is used by ditherInhibit to stop the dither, for example, during a MOT detection cycle. The inhmode input sets the initial and final phase of the gated dither, with 22.5° resolution, so the servo output is nominally settled when the dither ends.
lockIn.v: Lock‐in amplifier and modulation waveform synthesizer. The modulation is generated by twice integrating a step‐wise waveform,¹ which has no 3rd harmonic and small 5th and 7th harmonics, producing a near sinusoid and further reducing all harmonics. The module outputs both quadrature components of a demodulated input signal at 1f, 2f or 3f. The demodulation has no sensitivity to the 3rd harmonic of the input signal, at 3f, 6f or 9f, respectively.
ditherInhibit.v: Inhibits or enables a dither with a phase set by inhtrig, after an enable signal goes low or high.
dithSwitch.v: Alternately enables two dither modulations: while one dither is enabled, the other is inhibited. It can avoid interference between two dither error signals, as for 361 nm SFG. SelectableOutput<n>.v: Selects one of 0 to n‐1 signals, e.g., to monitor on an analog output. SelectableOutput15.v additionally leaves the output unchanged for selection value of 15. FM_MOT_PARAM_ASSIGN.v: Assigns one of 4 sets of parameters for different experiment configurations of FM_MOT.sv, selectable with the MOT display button.
FM_MOT.sv: Generates three arbitrary waveforms and instantiates a lock‐in detector and a gated integrator for DSP. We use the arbitrary waveforms as triggers and to modulate the frequency and amplitude of a VCO that drives an AOM. An input, from a photomultiplier, is connected to a gated integrator with a background subtraction.
Cd_Oven_PARAM_ASSIGN.v: An input, which is connected to a touchscreen button, selects one of three sets of temperature servo parameters, or disables the servo. Here, it is used to select the temperature setpoint for a Cd oven.
fmMOTmem.v: Parent module with two instances of ram_dual.sv to store two signals and cyclically output the stored values, e.g., to fast DAC outputs for display. As implemented, it stores the gated‐integrator output from FM_MOT.sv and the differences of its successive outputs. Debugging probes allow the stored values to be exported.
ram_dual.sv: Stores and reads signals from the FPGA Block RAM. The write‐enable, we, triggers the signal capture.
TempServos.v: Parent module with 10 variable duty cycle temperature PID servos. The servos can be connected to analog outputs or variable duty cycle generators. The variable duty cycle outputs

10

can control transistors to pulse heater currents, and they have synchronized delays for load diversity. We use a 125 kHz clock for our temperature servos.
temp_servo_startup_ramp.v: Module to slowly increase the temperature servo duty cycle with a time scale of order minutes, e.g., to slowly warm a non‐linear crystal. When the error signal changes sign, or the duty cycle reaches the preset, the ramp stops and holds its value, the PID is enabled, and its output is added to the held ramp output.
tempPID.v: A PID controller like CavServo.v, with DBS.v, the higher resolution variant of the differential filter, which has less timing margin.
DBS.v: Like DBS_rolloff.v, but with 25% resolution on all filter coefficients. It has timing margin for clock frequencies below 80 MHz for a filter word size (SIGNAL_SIZE + FB) of 40 bits.
tempPID_rolloff_bitshift.v: Like tempPID.v, except with 2N resolution for the filter frequency shifts.
tempPID_dg.v: Like tempPID.v, with debugging outputs: individual P, I and D filter outputs, their sum before and after rounding and after truncating fractional bits.
VDC.v: Generates a 1‐bit variable duty cycle output with an adjustable delay for load diversity. It instantiates FastAVG4.v to increase the precision of pulse‐width modulation temperature servos.
FastAVG4.v: Generates a sequence of 16 numbers that are added to the servo input to get sub‐cycle precision, 1/16 of a cycle resolution, for the variable duty cycle output.¹ The MSB alternates every cycle and the LSB switches every 8 cycles.
RelockLEDs.v: Generates signals to indicate if a servo is locked, unlocked, or unlocked in the past few seconds. It is used in conjunction with the display program to change the color of servo indicator buttons.
err2clrst.v: Sets the 2‐bit color state for temperature servo indicators.
display.v: Controls the LCD touchscreen. As described in more detail below, the display has buttons for controlling servos, the experiment state, and the Cd oven temperature, and it displays the status of cavity and temperature servos. The display.v code assembles the display commands into cmdarr and stores inputs from the display in readtemp. This module currently supports one display. The baseboard can support two independent displays, using the CS wires to alternately select each display, since the SDI and SDO wires are shared.
LCD_header.vh: A Verilog header file that contains the signal declarations, tasks and functions for display.v.
clr_str_4_st.v: Converts a 2‐bit color state from err2clrst.v into a string command for a display color.
gain_inc_trig.v: Formerly used module to adjust servo parameters using the display. A button selects a servo parameter to adjust and buttons on the display increment or decrement parameters.
Dec2Str1B.v: Changes a signed integer from ‐9 to 9 into a string for the display. It was previously used in conjunction with gain_inc_trig.v.

11

Two additional modules are included that are not instantiated in the default designs.

rmp_sml.v: Generates a triangle wave with an amplitude of 5 adjustable equal steps (nominally 1 LSB) and an adjustable offset. It is useful for measuring the fast DAC bipolar offset error. In the FAST DAC TESTING SECTION of top.sv, instances of it for each fast DAC are commented‐out. PIBS.v: A 2nd order proportional‐integral filter with a low‐frequency integral gain cap and a high‐ frequency roll‐down. The filter uses bitshift‐addition operations instead of multipliers and has a 25% gain resolution. The filter has upper and lower limits to prevent overflow and underflow. The module has an adjustable input and output signal size and an adjustable number of additional internal fractional bits. It allows timing margin below 70 MS/s for a filter word size of (SIGNAL_SIZE + FB) 57 bits.

### Touchscreen LCD Driver: display.v, LCD_header.v and SR_CTRL.v

The display (see Fig. 2) has 10 touch buttons to control the cavity servos, the Cd oven temperature, and the experiment sequence, which selects different output arbitrary waveforms. The cavity servo buttons change color depending on the cavity’s lock state, red if unlocked, yellow if relocked in the last five seconds, and a servo‐specific color if locked for more than five seconds. Pushing a cavity servo button cycles between the servo off state Stp, the scan state Scn, and the lock state, with its servo‐ specific name. The STOP SERVO button on the right side turns off all cavity servos except for the reference cavity lock of the 1083 nm laser. The Cd oven temperature servo has an OFF state and three different temperature setpoints: 99C, 119C, or an adjustable temperature setpoint. The Cd temperature servo button changes color depending on the temperature error signal; dark red and blue indicate high and low temperatures, and orange and light blue indicate high and low temperatures near the setpoint. The display also includes 10 temperature indicators (small squares below the top row of cavity servo buttons) for other temperature servos; these use the same color indicators as the Cd oven servo. The two rightmost indicators are used as monitors for the serial parameter reassignment and the fast ADC frames. The FM‐MOT button has four states: OFF, and SAT, MOT and MET, which have three independent sets of parameters for the VCO FM, laser intensity and MOT coil voltage outputs.
The display is controlled by display.v, which contains the sequential logic to output and read the display data. Display signals, functions and tasks are declared in a header file, LCD_header.vh. It is added to display.v with:

`include LCD_header.vh

after the module port declarations. The header file includes hex RGB color definitions for the button and temperature indicator colors, temperature indicator range parameters, memory addresses and other parameters for the display, and functions to format, initialize, and assign the serial data that is sent to the display. The parameters, functions, and data formatting are given in the graphics controller programmer’s guide.⁵ The sequential logic in display.v has two states, active for display

12

initialization and data_active for normal display operation. After initializing in the active state, it changes to data_active.
The bulk of the sequential logic in display.v updates the display and registers buttons that are pushed. The data sent to the display is loaded into cmdarr by calling the assign_displaylist task in LCD_header.vh. Touch buttons and indicators are specified by the button task. The touch buttons and indicators each have an identifying “tag” number, regtouchtag for the sequential logic. The program structure allows the display to be modified, including adding more control buttons.
The display is programmed and read through an SPI bus. The SPI bus includes a clock, SCK; the serial data input from the display, SDI; the serial output data, cmdarr, to the display, SDO; two chip select signals, CS0_OUT and CS1_OUT to select a display, potentially two independent displays; and a power down, PD_OUT. The baseboard has two DB9 connectors to support two independent displays. Additional displays without touch support can be connected in parallel. The display SPI signals are shift register inputs and outputs, which are controlled by the SR_CTRL.v firmware module. The 24‐bit shift registers are clocked at 50 MHz, which limits the update rate of any shift register I/O to 2 Mb/s, and therefore the SCK clock to less than 1 MHz. The cmdarr data is a total of 182, 57‐bit words, yielding a display update rate of 96 Hz. A pointer, bitcount, in SR_CTRL.v cyclically selects up to 24 I/O for the input and output shift registers. If fewer than 24 shift register I/O are used, the display update rate can be increased by decreasing the maximum bitcount to less than 24.
On some boards, we have observed occasional problems communicating with the display using the shift register I/O with display cables longer than 13 cm or long cables connected to other shift register outputs. These faults may be due to other shift register loads or marginal cable terminations. Normal function has always resumed after resetting the display via the serial line with reset.v. On our most used baseboard, no such problems occurred with a 70 cm cable – the shift registers on this baseboard used 5 V logic outputs, whereas the baseboard with occasional faults used 3.3 V. On the most recent baseboard design, an optional 5 V power connection has been added for the 3V3d.e power plane for the shift registers, with in‐series pads for potentially a ferrite bead and two diodes, to reduce the 5V supply voltage. Vias near the display connectors allow them to be powered independently by the usual 3.3 V source, again through ferrite beads.

## Firmware

A number of nominally static firmware modules capture incoming data, write data to the outputs, and perform baseline tasks such as generating clocks. After briefly describing each, additional detail is given for the ADC and DAC firmware, and finally the serial interface to reprogram parameters in real‐ time. The firmware uses several primitives, components native to the target FPGA’s architecture, e.g., flip‐flops, lookup‐tables, shift‐registers, RAM, multipliers, and I/O buffers. The UG953 user guide⁶ contains the templates for instantiating 7‐series FPGA primitives.

GlobalClocks.v: Generates the clocks used in the design from a 100 MHz clock on the Enclustra Mercury+ module. It uses a mixed‐mode clock manager (MMCM) 7‐series FPGA primitive. The

13

clocks’ frequencies and phases are set by their div and phs parameters, and mmcmloc selects the MMCM’s location.
FastADCsDDR.v: Parent module with five instances of LTC2194DDR.v for the LTC2194 fast ADC chips. The ADC’s are clocked by a shared ENC from the FPGA, generated by a source‐synchronous output clock architecture using the ODDR 7‐series FPGA primitive. The module sets the bit‐slips and fine delay tap values for each data line, which are normally calibrated during the initial testing of a baseboard. It also includes the two instances of the 7‐series FPGA primitive IDELAYCTRL and specifies their locations, so IDELAYE2 primitives can be used in LTC2194DDR.v.

7
LTC2194DDR.v: Firmware to drive an LTC2194 fast ADC. It deserializes the serial DDR data from the ADC using two phase‐shifted 400 MHz clocks. Each ADC uses an LVDS pair for its frame, to synchronize the data, and 2 LVDS data pairs for each channel, 4 wires per channel. One data pair transfers the odd bits and the other the even. These ADC’s are programmed via their SPI bus for 2’s complement output. This module contains: LVDS buffer instances; deserialization of the output with the 7‐series FPGA primitive ISERDESE2; five IDELAYE2 FPGA primitive instances to fine tune deserializer input delays; and the routing of the odd and even bits to form two 16‐bit words. The clock phases and line delay calibrations are described below. This interface is demonstrated up to 100 MS/s. UG471: 7 Series FPGAs SelectIO Resources⁷ has more details on the primitives in this module.
BitslipStatic.v: Enables the bit‐slip submodule of ISERDESE2 to apply a specified number of bit‐slips to align the incoming serial data.
BitslipDynamic.v: Enables the ISERDESE2 submodule to apply bit‐slips until the deserialized frame FR is 11110000.
FastADCs_SPI.v: Programs the LTC2194 chips over their SPI bus via SPI.v. It generates one CS signal that connects to the five CS wires for the chips on the baseboard, so all chips are programmed simultaneously and identically. (Each ADC could be programmed individually by selecting each CS successively.) SCK is also generated with a source‐synchronous architecture. To program the ADC’s, this module sends 5 data packets: the first resets the control registers; the second and third specify 2’s complement outputs over two LVDS pairs; and the final two data packets set a test pattern output, which can be used to output a known number when calibrating the ADC clock phases and data delays. It also sends a sleep command to all ADC’s, 30 s after the ADCOFF input goes high, and a wake‐up command when ADCOFF goes low and the ADC’s are asleep.
SPI.v: Derived from NIST module² that implements a four wire SPI bus.
FRmon.v: Monitors the deserialized frames from the fast ADC’s and outputs a status for a display indicator color. The displayed color is light blue if all of the frames have been 11110000 for more than 30 seconds, red if any of the five frames is not 11110000, and orange for 30 seconds after all become 11110000.
SlowADCs.sv: Parent module that includes LTC2335_16.sv and the 7‐series FPGA input and output buffer primitives, IBUF and OBUF, for the out‐of‐context slow ADC implementation (see “Synthesizing and Implementing Bitstreams” below). It also implements a source‐synchronous output clock with an enable.

14

LTC2335_16.sv: Firmware to capture data from two LTC2335‐16 ADC’s over an SPI bus. It selects the channel to be read on each conversion – both slow ADC’s on our baseboard share a single SDI input so they both read their same channel number (if sampling at their maximum rate). The baseline firmware reads the channels in the order {0, 1, 2, 3, 4, 5, 6, 7} as 2’s complement numbers.
SPI_LTC2335_16_seq_x2.v: This SPI variant waits an adjustable number of cycles after its chip select signal goes low, so that the timing requirements of the LTC2335‐16 are satisfied. The two CS wires to each ADC are connected to the same logic signal so both slow ADC’s are programmed simultaneously and identically.
FastDACs.v: Parent module containing seven instances of MAX5875.v, for the two‐channel fast DAC’s. The data of each DAC is interleaved at 200 MS/s for each of its channels updating at 100 MS/s. It implements a source‐synchronous output clock with an adjustable phase‐shift to meet the DAC timing requirements. The clock buffer locations are selected for this module instance’s specific out‐of‐context placement.
MAX5875.v: Interleaves the fast DAC data and generates a channel select signal. The default baseboard configuration sets the data to be 2’s complement.
SlowDACs.sv: Instantiates LTC2666x2.sv and the signal buffers for out‐of‐context implementation for the two LTC2666‐16 slow DAC’s, and includes a source‐synchronous output clock with an enable.
LTC2666x2.sv: Addresses two LTC2666‐16 multiplexed SPI DAC’s that share an SDI. These DAC’s have a specified maximum update rate of 50 kS/s. These DAC’s use offset binary, so this module inverts the MSB’s of the 2’s complement data to be sent to the DAC’s.
SPI_LTC2666x2.v: This SPI module alternately updates two slow DAC chips.
signFlip.v: Flips the sign of the slow ADC inputs and outputs to the slow DAC’s because their inputs/outputs have inverting amplifiers. Since the most negative 16‐bit 2’s complement number is ‐ 2¹⁵ and the most positive is 2¹⁵‐1, this module flips the sign, and applies an offset of 1 to yield a 1‐to‐ 1 mapping of the inputs to outputs.
serialLine.v: Captures input serial data at 100 kS/s, beginning and ending with 16‐bit handshakes. We use it to adjust parameters, which are sent as 27 sequential 35‐bit numbers, sandwiched between two handshakes.
serialHSmon.v: Like FRmon.v for the fast ADC frames, it monitors the handshakes from serialLine.v, and outputs a status for a display indicator color, to indicate matching handshakes (light blue), non‐matching handshakes (red), and no incoming data (dark blue), with handshakes of all 0’s or all 1’s.
SR_CTRL.v: Controls the 24‐bit shift‐register’s digital I/O, which includes the display control signals, associated with display.v. Its signals, bitcount and cnt_reset, are connected to display.v for synchronization.
SRB_CTRL.v: Controls the 16‐bit shift‐register B’s digital outputs.

We next discuss aspects of the firmware modules in more detail, including initial timing calibrations.

15

Fast ADC’s: LTC2194.v, LTC2194DDR.v, BitslipDynamic.v and BitslipStatic.v
The baseboard has 10 fast analog inputs connected to five LTC2194 fast ADC’s. Their data is transferred over a serial LVDS bus, a high‐speed differential signal interface with 100 Ω termination between the two LVDS wires, typically close to the receiver. The LVDS inputs to the FPGA use an on‐chip termination, specified in the input buffer primitive IBUFDS instances in LTC2194DDR.v.
The default design samples each fast ADC channel at 100 MS/s. Each channel uses two LVDS wire pairs; one pair for the odd bits of the 16‐bit word and the other for the even. An 8:1 FPGA deserializer receives the serial data from each pair at 800 Mb/s and outputs a parallel 8‐bit word at 100 MS/s. The 8‐bit words for the even and odd bits are then combined to form the 16‐bit sample. The FPGA deserializer primitive, ISERDESE2, is used in the double‐data rate (DDR) mode and clocked with a 100 MHz clock and two 400 MHz clocks with adjustable phases. The five fast ADC’s share a common 100 MHz LVDS encode (ENC) signal from the FPGA. The ADC’s sample on the rising edge of ENC+, with 7 ENC cycles of latency, 70 ns at 100 MS/s, from sampling to output. The firmware adds an additional 100 MHz cycle of latency. The ENC is AC‐coupled at each chip and the baseboard’s default termination is at a central point, with additional pads at each chip.
Calibrating the Fast ADC ISERDESE2 Delays
LTC2194DDR.v uses fine delays and bit‐slips to synchronize the capture of the serial LTC2194 conversion and frame data. The fine sub‐cycle delays are implemented with IDELAYE2 primitives. They can be incremented with an approximate resolution of 78 ps per tap delay, which is 1/32 of a cycle of the 400 MHz clock so the full range of 32 IDELAYE2 taps spans two bit‐slips. The bit‐slips of the deserialized data are applied by the bitslip submodule of ISERDESE2. Initially, after programming, the BitslipStatic.v firmware instances enable ISERDESE2 to apply a specified number of bit‐slips to each conversion data signal. Thereafter, the five instances of the firmware submodule BitslipDynamic.v continuously apply bit‐slips to the conversion and frame data to maintain each deserialized FR as 11110000.
To calibrate the ADC’s we apply a full‐scale triangle wave on each fast ADC input and sample the conversion and frame data with an Integrated Logic Analyzer (ILA), a Vivado IP core.⁸ With BitslipDynamic.v inhibited in LTC2194DDR.v, we randomly sample the 3D parameter‐space of the phases of the 100 MHz ADC ENC and the two 400 MHz deserializer clocks, relative to the 100 MHz deserializer clock. This yields a volume where the data are captured without glitches, although with likely incorrect bit‐slips. We then fix the ENC phase near the center of that volume and map the glitch‐ free region in the plane of the two 400 MHz clock phases. Next, the fine delays are scanned and centered in their glitch‐free range. It may be that the phase and fine delay adjustments have to be iterated. If all of the glitch‐free ranges of all of the fine delays are more than two taps, all of the delays can be reduced with a larger ENC phase, two taps for each phase increment of 5.625°. The final step is enabling BitslipDynamic.v and setting the static bit‐slips of each data signal, so that the MSB from the ADC is connected to the MSB of the output word. We found centered phases of (11.25°, ‐22.5°, ‐ 22.5°) for the ENC, 400 MHz, and secondary 400 MHz clocks, and centered taps between 8 and 24, with typical glitch‐free ranges of 13 taps. We note that our glitch‐free region is well outside of the specified

16

expected phases for the two 400 MHz clocks, 0 and 180°.⁹ The three phases are specified in top.sv and the taps in FastADCsDDR.v.
Finally, we note that we do not use the recommended synchronization for these ADC’s, which is to use the DCO clock from the ADC to capture the data with the FPGA. This capture method requires two clock‐capable FPGA input pairs per LTC2194 chip, one for FR to align the data and the other for DCO to latch the data, requiring an additional 10 clock‐capable pairs for our five ADC's. This method could potentially require fewer phase and delay adjustments.
Fast DAC’s: MAX5875.v
The baseboard has seven MAX5875 16‐bit DAC’s, providing 14 100 MS/s analog outputs. Each fast DAC uses 19 single‐ended LVCMOS inputs, 16 for data, a channel select, a clock, and a sleep mode control, which is connected to a shift register B output. On the baseboard, the fast DAC’s differential current outputs are terminated with 50 Ω and buffered by AD8421 instrumentation amplifiers with a default gain of 72 and an ±18 V output range. The MAX5875.v firmware uses the interleaved mode of the fast DAC’s, sending the data for both DAC channels over the same 16 data lines. The three fast DAC’s on FPGA connector B share a common 200 MHz clock from the FPGA and the four fast DAC’s on FPGA connector C share another 200 MHz clock, yielding 100 MS/s update rates. The latencies of the two channels of each DAC are 8 and 9 200 MHz clock cycles, 40 and 45 ns, and the firmware latency is one 100 MHz cycle.
Slow, Multichannel, Serial ADC’s: LTC2335_16.sv
The baseboard has 16 slow inputs connected to two LTC2335‐16 16‐bit ADC’s. Each slow ADC has 8 channels, which can be read in an arbitrary order at a maximum specified update rate of 1 MS/s, e.g., a single input can be updated at up to 1 MS/s or all 8 channels at 125 kS/s. They are controlled with an SPI bus, which uses a clock SCK with an adjustable phase shift, data input SDI, chip select CS for each chip, and data output SDO for each chip. The two ADC’s have five additional signals, a shared CNV to start conversions, a BUSY for each chip, which triggers the data transfer on the completion of an ADC conversion, and two PD power down’s, which are connected to shift‐register B outputs. Both slow ADC’s share a single SDI baseboard wire and the default firmware connects both CS’s to the same logic signal. Therefore, both chips read their same channel number when sampling at their maximum rate. The baseline firmware reads the channels in the order, {0, 1, 2, 3, 4, 5, 6, 7}, and sets the format as 2’s complement via the SPI bus. Because the slow ADC’s share a SDI, reading channels in an arbitrary order on each chip requires addressing each with its own CS enabled, and then addressing the other slow ADC. The maximum update rate is a combined 1 MS/s for both chips, e.g., updating both at 0.5 MS/s or just one at 1 MS/s, as opposed to a combined 2MS/s when reading the same channels on both, e.g, updating all 16 channels at 125 kS/s. An alternative mode is programming the internal sequencers of the ADC’s to repeatedly read an arbitrary pattern of up to 16 configurations at 1 MS/s on each ADC. Commented out code to program the sequencers is included.
Slow, Multichannel, Serial DAC’s: LTC2666x2.sv
Two LTC2666‐16 slow DAC’s on the baseboard provide 16 analog outputs and are controlled with an SPI bus, with a CS for each chip, and a shared SCK, SDI and SDO. The channels can be written in an

arbitrary
DAC’s use
The slow
but overc
observed
has an of
n0 and n1
The s
the baseb
steeper ro
amplitude

### Adjustin

The s
triggered,
numbers,
updated.
LBO cavity
We us
and trigge
associated
program
repository
use more

FIG. 5. Se
serial stre
handshak

## Progra

We p
provided
baseboard

order; the ba
e offset binary
DAC’s have a
locking produ
the zero‐cro
fset of order
. The offset c
low DAC’s als
board has 5th
oll down abo
e is less than

### g Paramete

erialLine.
, serialLin
sandwiched
top.sv spe
y lock is num
e a Stanford
er. It connect
d visual basic
uploads to t
y.

4 Implemen
FPGA resour

rial data tran
eam of 27 seq
kes that specif

## mming th

rogram the F
bitstream, (d
d and compu

aseline firmw
y, so this mod
specified ma
uces a signific
ossing offset i
8 LSB. The L
compensatio
so have intrin
order filters
ove 300 kHz,
2 LSB, and th

### ers with seri

.v module c
ne.v capture
between ma
cifies a hand
ber 20 and o
Research Sys
ts to the FPG
c macro enco
the DS345 vi
nting USB or
ces.

nsfer. An exte
quential 35‐bi
fy the parame

## he FPGA

FPGA via its J
disconnect an
ter, and ope

ware⁴ updates
dule inverts t
aximum upda
cant zero‐cro
increasing wi
LTC2666x2.
n is comment
nsic update gl
on the slow
while mainta
e glitch impu

### alLine.v

captures seri
es bits at 10
atching 16‐bi
dshake_def
ur Reference
tems DS345 a
A through tw
odes parame
a GPIB. The
ethernet con

ernal trigger in
t numbers, {x
eters to upda

JTAG port wi
nd then) app
en the Vivado

s the slow ou
the MSB’s of
ate rate of 50
ssing offset. W
th update ra
sv module c
ted‐out in the
itches on the
w outputs to
aining less th
lse is 15 LSB∙

ial input dat
00 kb/s and
t handshakes
ault, to wh
cavity tempe
arbitrary wav
wo buffered d
eters in an ar
Excel files a
nnections wit

nitiates the se
1, x2, …, x27}
ate.

ith a USB‐JTA
ly power to t
o Hardware M

utputs in orde
the 2’s comp
0 kS/s. They c
We tested up
te as 16 LSB/
an compensa
e baseline firm
eir outputs. T
suppress freq
han π/4 phas
µs.

ta used for
partitions th
s (Fig. 5) that
hich the “serv
erature servo
veform gener
digital input l
rbitrary wave
and LabVIEW
h the FPGA a

erial upload o
}, begins and

AG adapter, D
the baseboar
Manager. Clic

er, {0, 1, 2, 3
plement data
can be updat
pdate rates of
/(MS/s) – up
ate this offse
mware.
To reduce the
quencies abo
se lag below

parameter a
hem into 27
t specify the
vo number” i
is number 3
ator to gener
ines. An Exce
eform text fil
W program ar
are other opt

of adjustable
ends with ide

Digilent JTAG
rd, connect t
ck the “Auto

, 4, 5, 6, 7}. T
sent to the D
ted at higher
f up to 2 MS/
dating at 500
t, using the i

glitch amplit
ove 50 kHz, w
10 kHz. The

adjustment. W
sequential 3
parameters
is added, e.g
3.
rate the seria
el spreadshee
le that a Lab
re available i
tions, which

parameters.
entical 16‐bit

‐HS3. To loa
the adapter t
Connect” sho

17

These
DAC’s.
rates,
/s and
0 kS/s
nputs

tudes,
with a
glitch

When
35‐bit
to be
g., our

l data
et and
bVIEW
n the
might

The

ad the
to the
ortcut

18

and then the “Program” shortcut in the “Hardware” window, select the bitstream, e.g., top.bit, from its file location in the pop‐up menu, and click the “Program” button (both of these may appear in the green bar above the Hardware window). The provided design has an ILA debugging probe and Vivado will automatically add a top.ltx probe in the same directory when top.bit is selected. After the bitstream is loaded, the debugging probes file can be reloaded by right clicking on the FPGA in the Hardware window and choosing top.ltx as the probes file. UG908: Vivado Design Suite User Guide Programming and Debugging¹⁰ and UG936: Vivado Design Suite Tutorial Programming and Debugging¹¹ have further information and a detailed tutorial.

### Flash Programming

The Mercury+ KX2 module has on board flash memory that can store a bitstream to automatically load at FPGA power up. To program the flash memory, switch the BOOT_MODE control line on the baseboard to logic‐high SLAVE mode. With the FPGA connected, in the Vivado Hardware Manager right click to “Add New Memory Configuration Device.” Select the Spansion s25fl512s flash chip of this FPGA module in the menu window. The flash chip should then appear in the device hierarchy in the “Hardware” window of the Vivado Hardware Manager.
To generate the memory configuration files, select “Generate Memory Configuration File” from the “Tools” drop‐down menu in the top bar, select the memory part as s25fl512s, select an output configuration (.mcs) file name, select the SPI×4 interface, check the “Load bitstream files” box and select the bitstream file to load, check the “Overwrite” box, and click OK. This will generate the .mcs and associated .prm file. To program the memory, right click on the s25fl512s flash chip in the device hierarchy in the Hardware window and select the generated .mcs and .prm files. At this point, the bitstream can be manually loaded from the flash memory with the Hardware Manager. Alternatively, it can be automatically loaded from flash after a power cycle, with the BOOT_MODE switch in logic low FLASH mode. Note that the bitstream will not load from flash memory if the FPGA’s JTAG port is connected to a computer. For additional discussion see UG908,¹⁰ Chapter 5: Programming Configuration Memory Devices.

## Synthesizing and Implementing Bitstreams

### Quick Start Guide and Summary

This project uses Hierarchical Design (HD) flow to implement a number of firmware modules, and the display and FM‐MOT modules out‐of‐context (OOC), which synthesizes and implements the OOC modules before the full design. This can reduce the time to synthesize and implement the entire design and provides consistent placement and routing of these OOC modules on the FPGA, and thereby likely gives more reproducible timing margins. A detailed discussion of executing each step of synthesis and implementation follows this quick start guide. The project in the repository⁴ includes implemented OOC modules.

Generating Tcl scripts. The Tcl_Script_Generator.tcl script creates scripts to generate bitstreams from the provided MCFS firmware and software. The generating script uses files from the UG946:

19

Vivado | Hierarchical | Design | Tutorial | version | 2014.1, | which | can | be | obtained | from
https://secure.xilinx.com/webreg/clickthrough.do?cid=356076&license=RefDesLicense&filename=ug94 6‐vivado‐hierarchical‐design‐tutorial.zip. This link will prompt the user to sign a Xilinx Design License Agreement before the files can be downloaded. After extracting the 14 Tcl files, replace c:/MCFS_HD/UG946 in Tcl_Script_Generator.tcl below with the reference design root directory, which contains the extracted file design_complete.tcl. Entering the command below in the 2020.1 Vivado Tcl Shell will generate the Tcl scripts variants for the provided MCFS firmware and software from the downloaded Xilinx reference design.

source Tcl_Script_Generator.tcl ‐notrace

Top‐level synthesis and implementation. To synthesize and implement the design without changing the OOC modules, e.g., for many changes in top.sv or CavServos.v, use the following command in the Vivado Tcl Shell:

source MakeBitstream.tcl ‐notrace

This runs the MakeBitstream.tcl script, which executes the design.tcl script and copies useful files to the Implement/BIT/dump directory. The design.tcl script, whose steps are described in more detail throughout this section, specifies the already implemented OOC modules and the steps to synthesize and implement the full design without resynthesizing or reimplementing the OOC modules. It generates a bitstream to be loaded onto the FPGA in of order 40 minutes.

Top and OOC synthesis and implementation. To synthesize and implement modified OOC modules, the MakeOOC.tcl script executes design_ooc.tcl, a variant of design.tcl with run.topSynth, run.oocSynth, run.tdImpl and run.oocImpl set to 1. MakeOOC.tcl also backs up previous OOC synthesized and routed design checkpoints (DCP’s) before sequentially running the above flow steps to resynthesize and reimplement the OOC modules. The design_ooc.tcl script uses a variant of top.sv located in Sources/hdl/ooc that prevents unwanted optimization that would fix OOC module ports. For example, the top.sv variant yields a SlowADCs.sv OOC implementation with all of its ports adjustable, including the channel sampling sequence. If SlowADCs.sv was synthesized and implemented OOC with the slow ADC channel sequence of the default top.sv, the module ports that pass the sampling sequence to SlowADCs.sv would be fixed; changing the sequence would then require rerunning the SlowADCs.sv OOC synthesis and implementation, as well as the top level MakeBitstream.tcl.
The following commands reimplement all OOC modules and generate a bitstream:

source MakeOOC.tcl ‐notrace

followed by

20

source MakeBitsream.tcl ‐notrace

The OOC modules in this project are the slow ADC firmware (SlowADCs.sv), the fast and slow DAC firmware (FastDACs.v and SlowDACs.sv), the FM‐MOT module (FM_MOT.sv), the display module (display.v) and the shift‐register firmware (SR_CTRL.v) for the displays, temperature servo outputs and other digital I/O. Implementing the display module OOC saves considerable time during synthesis and implementation of the full design and the four OOC interface modules are rarely modified. We also tried to implement the fast ADC firmware (FastADCs.v) OOC but were unsuccessful. This could be due to the fast ADC firmware using IDELAYCTRL groups, which are not fully preserved in HD.¹² We note that generating modules OOC does not always make bitstream generation more efficient – implementing the cavity or temperature servos OOC did not reduce the time for the top level synthesis and implementation.

### Hierarchical Design (HD) Flow

We now discuss HD Flow, and then the synthesis and implementation of the OOC modules and the full design using design_ooc.tcl and then design.tcl Tcl scripts that run in the Vivado Tcl Shell. If there are no changes to the OOC modules, they do not have to be resynthesized and reimplemented, and one can proceed directly to the “Top Implementation” section below for guidance on modifying the default design.tcl script. Note that there is no GUI for the HD flow. In contrast to project flow, the HD flow can define the physical locations on the FPGA of selected module instances. More information on HD is available in the user guide, UG905: Vivado Design Suite User Guide Hierarchical Design,¹² and the tutorial, UG946: Vivado Design Suite Tutorial Hierarchical Design.¹³ Our HD project for the MCFS is adapted from the tutorial design.

### Hierarchical Design .prj Files

The Tcl scripts specify the names of .prj files that must list all of the modules to be synthesized. For top‐level synthesis, top.prj lists all of the modules except those that are instantiated in only OOC modules. Modules that are implemented OOC have to be designated in top.prj using dummy modules, called black boxes or stub files. A black box only declares the module’s ports, which define that OOC module’s connections to the rest of the design. During top‐level implementation, the placed and routed OOC modules are inserted into the black box locations. The design_ooc.tcl script has to similarly specify additional .prj files that list all the OOC modules to be synthesized, including their submodules that may not appear in top.prj. The .prj files are located in the Sources\prj directory.

### OOC Module Synthesis

Top‐level synthesis with black boxes precedes OOC synthesis, which interprets the HDL code for implementation in a specified physical FPGA location. Here, as an example, we specifically describe the OOC module synthesis of the display module, display.v. In design_ooc.tcl, each OOC module has a subsection with the heading “OOC Module Definition and OOC Implementation.” The

21

display section begins with the assignment of module name display to the variable module0 and, for the other OOC modules, the sections are similar, albeit with different variables, e.g., module1, module2…. The section also specifies display.prj and a directory Synth\display for this module’s OOC synthesis, and designates the instance name disp0 that is in top.sv. There can be multiple instances of an OOC module, and all of these can use the same OOC synthesized design checkpoint (DCP), but each instance requires a unique name and physical FPGA location for OOC implementation. The final few lines of the display section of design_ooc.tcl declare the names of the constraints .xdc files. These will be created during Top‐Down implementation and contain the physical optimization and timing constraints for the disp0 instance.
The provided design_ooc.tcl script successively runs topSynth, oocSynth for all OOC modules, tdImpl, and oocImpl for all OOC modules. This script specifies variables to control the HD flow steps to synthesize and implement the OOC modules. For example, modifying display.v without changing its ports only requires running the OOC synthesis and implementation for display.v, without resynthesizing and reimplementing the other OOC modules. To run only OOC synthesis for display.v, the values of the flow control variables in design_ooc.tcl are set as:
- run.oocSynth is set to 1.
- run.topSynth, run.tdImpl, run.oocImpl, run.topImpl and run.flatImpl are set to 0.

Additionally, the synth attributes of the other OOC modules must be changed to 0 in design_ooc.tcl. The line in each OOC Module Definition section ending with
${run.oocSynth} and each OOC Implementation line ending with ${run.oocImpl} can be commented‐out and the following line ending in 0 uncommented.
When the MakeOOC.tcl script runs design_ooc.tcl, with the above modifications and the value of the synth attribute for the display module is unchanged, it will synthesize only display.v and preserve the synthesized DCP’s for the other OOC modules. MakeOOC.tcl backs up the OOC constraints and the synthesized and routed DCP’s before design_ooc.tcl overwrites any.

### Top‐Down Implementation for OOC Implementation

Top‐Down implementation is an intermediate step between OOC synthesis and OOC implementation. It creates the constraints files that define the OOC modules’ timing characteristics and the connection points between the rest of the design and the Pblocks containing the OOC module. If a modified OOC module’s ports are unchanged, Top‐Down implementation does not need to be repeated and flow can proceed to the implementation of the OOC module(s). The Pblock for an OOC module is the physical area reserved on the FPGA for its logic elements and routing, and must be defined for each OOC module before running Top‐Down implementation. One method to set a Pblock’s parameters is:

1. Implement the full design with the module not OOC.
2. Open the routed DCP, top_route_design.dcp in the Implement\top directory.

22

3. In the netlist window, right click on the module instance that will be implemented OOC and select “Highlight leaf cells.” The cells associated with that instance should be highlighted in the chosen color.
4. In the device view window click “Draw Pblock” and draw a rectangle enclosing the highlighted cells. If the cells are spread too widely, or there is a risk of overlapping another Pblock, draw a Pblock that encloses most of the cells and will be large enough to contain all of the module’s logic.
5. Right click on the Pblock in the device view window and click “Pblock properties”. In the “Pblock Properties” window, click the “Properties” tab and copy the values in the DERIVED_RANGES field.
6. In the Sources\xdc directory, open top_flpn.xdc. It should contain all the constraints in top.xdc and the Pblock definitions for the OOC modules.
7. Create the Pblock constraints by pasting the DERIVED_RANGES values as the argument of the resize_pblock command (line 3 below), and substituting the instance name, e.g., disp0 for display.v, as follows:

1 create_pblock pblock_disp0
2 add_cells_to_pblock [get_pblocks pblock_disp0] [get_cells ‐quiet [list disp0]]
3 resize_pblock [get_pblocks pblock_disp0] ‐add{RAMB36_X1Y0:RAMB36_X6Y5\
4 | RAMB18_X1Y0:RAMB18_X6Y11 \
5 | DSP48_X0Y0:DSP48_X5Y11\
6 | SLICE_X12Y0:SLICE_X109Y32}
7 set_property CONTAIN_ROUTING 1 [get_pblocks pblock_disp0]
8 set_property HD.PARTPIN_RANGE {} [get_pins {disp0/*}]
8. Change the value of run.tdImpl to 1 and the values of the other flow control variables to 0 in design_ooc.tcl, and then execute MakeOOC.tcl to run Top‐Down implementation.
9. If an HD.PARTPIN_RANGE property was not defined, as in the above template, a suggested HD.PARTPIN_RANGE will be displayed in the shell window after the script finishes. Paste
this | suggested | range | into | the | empty | brackets | {} | after | set_property
HD.PARTPIN_RANGE, as in line 8 above, for its use in OOC implementation.

As previously mentioned, Top‐Down implementation creates several constraints files that define the connection points, timing constraints and optimization for the OOC modules. It can be helpful to inspect these constraints files located in Sources\xdc, particularly ones with names like <instance_name>_ooc_optimize.xdc. Those files may contain entries such as:

set_logic_zero [get_ports {port_name[3]}]

where port_name[3] denotes bit 3 of the port_name signal of the OOC module, which will always be 0 here. If this port should be adjustable, a possible solution is adding a (* DONT_TOUCH *) directive

23

before the declaration of the signal that is being set to zero in the top‐level or OOC module – see top.sv for examples. If the incorrect constraint remains after rerunning topSynth, oocSynth for the associated module, and tdImpl, another option is making the signal adjustable in the variant of top.sv in Sources\hdl\ooc. The design_ooc.tcl script targets this modified version of top.sv that avoids fixing any OOC module’s ports.

### OOC Implementation

With a valid Top‐Down implementation, an OOC module can be implemented by setting the value of the run.oocImpl flow control variable to 1 and the others to 0 in design_ooc.tcl. Within the OOC module’s subsection, its impl attribute should retain its default value, ${run.oocImpl}. For the modules that are not to be implemented, the ${run.oocImpl} line should be commented‐out and the following line should be uncommented so the values of their run.oocImpl flow control variables are set to 0.

When the ooc preservation attribute, which directly follow the specification of impl, is set to routing, the OOC module’s placement and routing are preserved when it is added to the full design during the final top‐level implementation. If there are routing conflicts between the top‐level module and an OOC module, they may be resolved by changing the instance’s preservation to placement, which locks the placement and not the routing. When preservation is set to placement, the OOC module’s routing is used as a starting point for the final top‐level implementation. We have observed routing failures when implementing the full design with OOC SlowDACs.sv with routing preservation; with only placement preservation the top‐level implementation reliably routes. Additionally, if the routing conflict is due to congestion, e.g., because the OOC module’s elements are restricted to be within a Pblock, shifting the Pblock’s boundaries so that there are unconstrained regions between adjacent Pblocks may ameliorate the conflict.

### Top Implementation

The final flow step is top‐level implementation, which optimizes, places, and routes the non‐OOC logic and integrates the implemented OOC modules. The default design.tcl script has default flow control variable values that ultimately yield a bitstream.

- run.topSynth and run.topImpl are set to 1.
- run.oocSynth, run.tdImpl, run.oocImpl and run.flatImpl are set to 0.

An example where topSynth is disabled is discussed below.
The Top Definition section of the default design.tcl defines the top‐level module and then specifies the implementation steps to run. The steps executed during top‐level implementation are again controlled by attributes, as for OOC synthesis and implementation, with the below defaults.

1 # Attributes that control top‐level implementation steps.
2 set_attribute impl $top | link | 1

24

3 set_attribute impl $top | opt.pre | "$tclDir/make_debug.tcl"
4 set_attribute impl $top | opt | 1
5 set_attribute impl $top | place | 1
6 set_attribute impl $top | phys | 1
7 set_attribute impl $top | route | 1
8 set_attribute impl $top | bitstream.pre "$tclDir/write_ltx.tcl"
9 set_attribute impl $top | bitstream | 1

With the link, opt.pre, opt, place, phys, route, bitstream.pre, and bitstream attributes set as above, the link_design, pre_opt_design_script, opt_design, place_design, phys_opt_design, route_design, pre_write_bitstream_script and write_bitstream flow steps run successively. The link_design step links the OOC and the top‐level netlists and constraints files to the target XC7K160T FPGA. A netlist file describes the components and connectivity of the FPGA design, which are given in the OOC and top‐level DCP files. The pre_opt_design_script executes the specified make_debug.tcl script, which adds ILA debugging probes to read the stored gated‐integrator DSP signals of the FM‐MOT module. The opt_design step optimizes the netlist for the target FPGA, potentially simplifying the design before placement and routing. The place_design step specifies the design ports and logic cells to resources on the target FPGA. The phys_opt_design optimizes placements of the post‐placement netlist to improve timing margins. The route_design step completes the logic by connecting the placed components. The pre_write_bitstream_script executes the write_ltx.tcl script, which generates the debugging probes file, top.ltx, before write_bitstream generates the FPGA bitstream top.bit. DCP files are created after the link_design, opt_design, place_design, phys_opt_design, and route_design steps.

### Debugging Probes

The Xilinx IP Catalog includes an Integrated Logic Analyzer (ILA) for debugging probes for sampling real‐time internal FPGA signals. Chapter 10 of UG908 (page 114) describes several ways to add debugging probes to a design.¹⁰ The highest‐level approach adds debugging probes using the ILA wizard, which creates a Verilog Instantiation Template, which may be added to the user’s code, like any other module. For HD flow, we instead use Tcl XDC debug commands, in the default make_debug.tcl script, to add the debugging probes to a DCP file’s netlist with no modifications to the HDL code.
To generate Tcl debug commands, we interactively add the debugging probes in the Vivado GUI. With the values of the flow control variables run.topSynth and run.topImpl set to 1, and the attribute settings below, the HD flow is stopped after the link_design step so the desired signals for debugging can be selected from the netlist in the created top_link_design.dcp file.

# Attributes that control top‐level implementation steps.

set_attribute impl $top | link | 1
# set_attribute impl $top | opt.pre | "$tclDir/make_debug.tcl"

set_attribute impl $top | opt | 0
set_attribute impl $top | place | 0

25

set_attribute impl $top | phys | 0
set_attribute impl $top | route | 0
# set_attribute impl $top | bitstream.pre "$tclDir/write_ltx.tcl"

set_attribute impl $top | bitstream | 0

The top_link_design.dcp file contains all the signals in the design, including those in OOC module netlists. With top_link_design.dcp open in the Vivado GUI, the design signals are listed in the “Netlist” window and can be selected for debugging by right clicking on the signal and choosing “Mark Debug.” After all desired signals are selected, open the “Tools” menu and select “Set Up Debug….” In its pop‐up window, the sampling clocks can be specified for each of the signals in the “Clock Domain” field of the “Nets to Debug” section. The number of samples to capture is set in the following “ILA Core Options” window. When “Finish” is clicked, Tcl commands will execute and add the debugging probes to top_link_design.dcp. Those Tcl commands include the sampling parameters and can be copied and pasted from the “Tcl Console” window into a script file, such as make_debug.tcl, so that these debugging probes will be automatically added in the pre_opt_design_script step in future HD flow executions.
Here, after top_link_design.dcp is saved, implementation can resume with the opt_design step and finish with write_bitstream, by setting the values of the design.tcl flow control variable run.topSynth to 1 and Top Definition attributes as follows:

# Attributes that control top‐level implementation steps.

set_attribute impl $top | link | 0
#set_attribute impl $top | opt.pre | "$tclDir/make_debug.tcl"

set_attribute impl $top | opt | 1
set_attribute impl $top | place | 1
set_attribute impl $top | phys | 1
set_attribute impl $top | route | 1
set_attribute impl $top | bitstream.pre "$tclDir/write_ltx.tcl"
set_attribute impl $top | bitstream | 1

### HD Flow Examples to Modify display

Here we give two examples of script modifications to resynthesize and reimplement a modified display.v, with no changes to other OOC modules. If the ports of display.v are unchanged, setting the values of the run.oocSynth and run.oocImpl flow control variables to 1 and the others to 0 in design_ooc.tcl will rerun only OOC synthesis and OOC implementation. The default attributes for display for synth and impl allow OOC synthesis and OOC implementation to run. To prevent resynthesis and reimplementation of the other unchanged OOC modules, set the values of their synth and impl attributes to 0 (including making their preceding lines comments), as in the display example in “OOC Module Synthesis” above.

26

If the ports of display.v are changed, the top‐level synthesis and top‐down implementation must be rerun, in addition to OOC synthesis and OOC implementation. Before top‐level synthesis, the ports of display’s black box module, Sources\hdl\blackbox\display_bb.v, will have to change to match those of the modified display.v. Note that the top.sv variant for design_ooc.tcl may also need to be modified to avoid the ports of display.v being fixed. The default values of the flow control variables in design_ooc.tcl should not change and the values of the synth and impl attributes, for display and the other OOC’s, should be set as in the above example for unchanged ports.
After setting the values of the flow control variables and the attributes of either example, running MakeOOC.tcl will reimplement display.v for this and any future bitstreams, and then MakeBitsream.tcl will generate an updated bitstream.

### Fast ADC Calibration Scripts

We provide additional Tcl scripts to automate generating bitstreams for calibrating the Fast ADC clock phases and fine delay tap values. The multiphase.tcl and multitap.tcl scripts execute design.tcl multiple times, saving files, including bitstreams and debugging probes files, for each run in Implement\BIT\dump. The scripts are in the FastADCcal directory and can be executed with:

source FastADCcal/multiphase.tcl ‐notrace

and

source FastADCcal/multitap.tcl ‐notrace

Here, the top‐level module, top_fADC.sv, is a minimal version of top.sv that contains the firmware for the fast ADC’s, fast DAC’s (OOC), and shift‐register B, which control the fast DAC’s power‐ downs. The multiphase.tcl script successively sets the phases of the fast ADC ENC and two 400 MHz clocks in top_fADC.sv with the values in phases.sv. It will generate a bitstream, with debugging probes for the fast ADC conversion data and deserialized frames, for each set of phases in phases.sv. Similarly, the multitap.tcl script successively sets the delay taps in FastADCsDDR.v to the fine delay tap values in taps.sv, generating a bitstream for each set. These scripts can be modified to automate generating other series of bitstreams.

### Suggestions on Debugging HD Flow

Here we compile some tips on debugging HD projects. The Xilinx user guide and tutorial have additional information.¹²,13 A number of useful checks are:

1. After running topSynth, the OOC modules should be black boxes in the synthesized design checkpoint, and have all required signals, e.g., on the black box modules.
2. After running oocSynth, the recently synthesized module(s) will have synthesized DCP(s), which should contain all of the input and output signals with their expected number of bits indicated.

27

3. After running tdImpl, there should be four constraints files associated with each OOC module instance in the Sources\xdc directory. One of these is
<instance_name>_ooc_optimize.xdc. It includes constraints that fix the module’s I/O that are static or unused in top.sv. If any of these signals are to be adjustable, the OOC module or top.sv should be modified.
4. After running oocImpl, the routed DCP for the OOC module can be checked as in step 2.
5. After running topImpl, all logic should be placed and connected in the routed DCP. If an OOC module causes top implementation to fail in the routing stage, relaxing its preservation attribute from routing to placement, as described in the “Top Implementation” section above, may allow the design to route successfully.

## Power supply board

The MCFS power supply³ uses a combination of switching and linear regulators to generate the 1.8 V, 2.5 V, 3.3 V, 5 V, ±15 V and ±18 V supply voltages for the baseboard from a single +15 V input. Table 2 lists the supply voltages shown in Fig. 6, and the approximate current used by each chip or device. To reduce switching frequency harmonics and their impact on the experiment, we use high switching frequencies, separate the power supply board from the baseboard, connect the supply voltages with twisted wire pairs wrapped around toroidal ferrite cores, and have a second stage of linear regulators for analog components. We use an I6A24008A033V‐N01‐R¹⁴ module to generate -20 V. Its switching frequency is 380 kHz, and we choose frequencies greater than 600 kHz for the other switching chip regulators.

28

TABLE 2: Chip Voltages and currents
Purpose | Power Supplies (V) | Est. current (mA)
FPGA module power | 15 (switching) | 175
FPGA I/O bank 13, 15 and 16 (for fast DAC’s, slow ADC’s and DAC’s, shift register B outputs, and FPC connector) | 3.3 (switching) | 250
FPGA I/O bank 12 and 14 (for fast ADC’s, shift register I/O, and JTAG) | 2.5 (switching) | 350
Fast ADC’s (LTC2194) | 1.8 (linear & switching) | (205 & 32) × 5
Voltage reference for fast ADC’s (ADR127) | 3.3 (linear) | 0.1 × 5
Fast ADC SPI pull‐up | 2.5 (switching) | 1
Fast input amps (OPA228) | ±18 (linear) | ±4.5 × 10
Fast input differential amps (LTC6406) | 3.3 (linear) | 220
Fast DAC’s (MAX5875) | 3.3 (linear & switching) 1.8 (linear & switching) | (58 & 3) × 7 (32 & 25) × 7
Fast output amps (AD8241) | ±18 (linear) | ±36 × 14
Slow ADC’s (LTC2335‐16) | ±15 (linear) 5 (linear) 3.3 (switching) | (+4.5/-5) × 2 14.5 × 2 4.2 × 2
Voltage reference for slow ADC’s (LTC6655‐4.096) | 5 (linear) | 7.5 × 2
Slow input quad amps (AD8513) | ±18 (linear) | ±8.45 × 4
Slow DAC’s (LTC2666‐16) | ±15 (linear) 5 (linear) 3.3 (switching) | ±5.5 × 2 6.5 × 2 0.002
Slow output amps (LF356) | ±18 (linear) | ±10 × 16
Digital buffers (TXS0108E‐Q1) for shift‐registers | 3.3 (switching) 2.5 (switching) | 0.006 × 2 0.002 × 2
Digital buffer (TXS0108E‐Q1) fast digital I/O | 5 (switching) 3.3 (switching) | 0.006 0.002
Shift register I/O (74LV165A /74VHC595) | 3.3 (switching) | 0.02 × 3 / 0.08 × 5
JTAG power | 2.5 (switching) | 50
Clock buffer digital side power (LTC6752) | 2.5 (switching) | 5

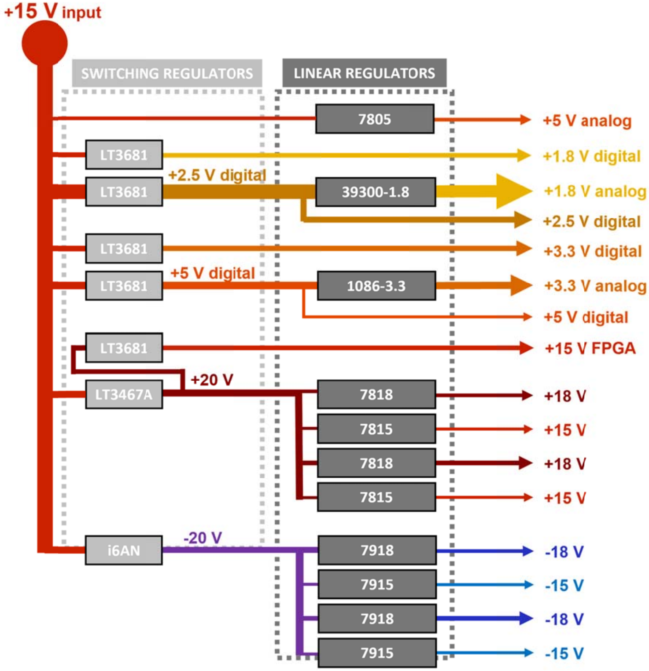
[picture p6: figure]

2BFIG. 6. MC
and DAC’s
frequenci
(+20 V), a

CFS power su
s, and the two
es are 600 kH
nd 380 kHz (‐

upply overvie
o ±18 V supp
Hz (1.8 V and
20 V).

ew. The powe
lies power th
2.5 V digital),

er supply has
e input and o
, 800 kHz (3.3

separate ±15
output amps.
3 V, 5 V, and +

5 V for the slo
The switchin
+15 V digital)

ow ADC’s
ng
, 2.1 MHz

29

## Assem

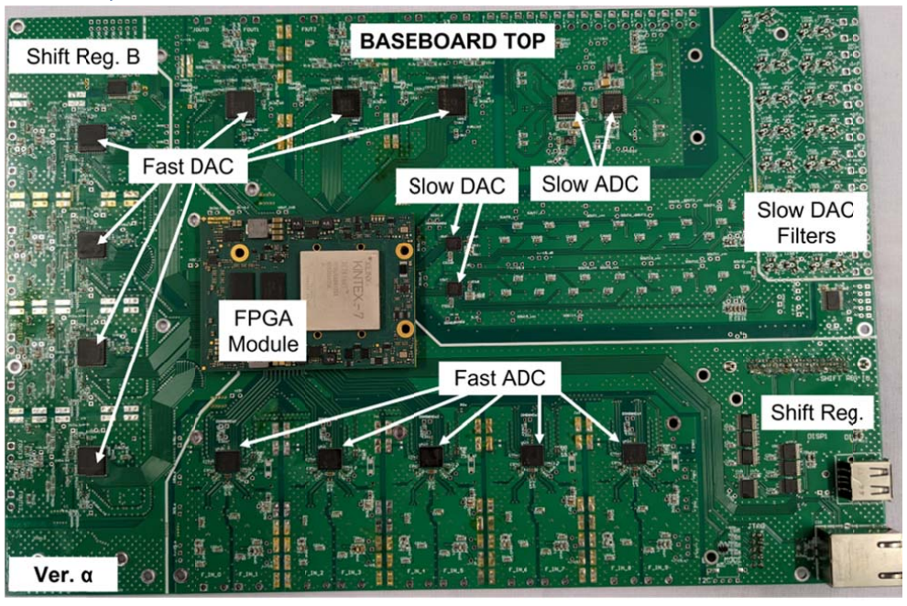
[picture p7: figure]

FIG. 7: To
including t
close to a
package.

## bly notes

op of assemb
he ADC’s and
vertical heat

bled baseboa
DAC’s, and the
spreader on t

ard. The top
e connectors fo
he side of the

layer of the b
or the FPGA m
e box that pas

baseboard has
module. When m
ssively heatsink

most of the
mounted in th
ks the board,

digital compo
e chassis, this
especially the

30

onents,
side is
e FPGA

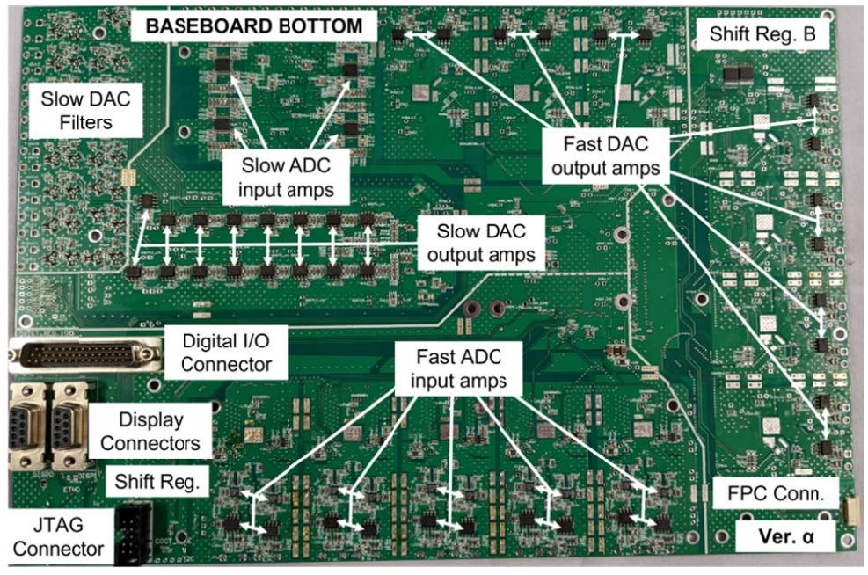
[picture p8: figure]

FIG. 8: Bo
including m
These are
potential e
FPGA lines

We m
cable to B
inputs and
connecto
a 13” long
dissipate
package i
internal te

## USB, Et

The M
connected

ottom of asse
many passive c
accessible wh
expansion, e.g
s that control t

mount the ba
BNC bulkhea
d outputs fro
r on the base
g section of 1
heat and a
n Fig. 7 to a
emperature n

## thernet, M

Mercury+ KX2
d the USB UA

embled baseb
components to
hen the board
., to add a fut
he shift registe

aseboard in a
d connectors
om the shift‐r
eboard (Fig. 8
1.5” angle alu
2”×2”×1/4” a
4”×4” chass
near 66°C.

## Multi‐Giga

FPGA modu
ART to a USB‐

board. The bo
o adjust gains
is mounted in
ure daughterb
ers have access

17” x 10” x
s on the fron
registers are c
). The power
uminum. Bot
aluminum bl
sis‐mounted h

## abit Trans

ule has a USB
A connector

ottom layer of
and frequency
n the chassis.
board with add
sible connectio

x 5” aluminu
nt and back o
connected to
r supply boar
h circuit boa
ock with a s
heat spreade

## sceivers

B UART and t
and one Ethe

f the board ha
y responses, a
The baseboa
ditional slow A
ons.

m chassis an
of the chassi
BNC connec
d and the lin
rds are moun
small air gap
r. This passiv

two Ethernet
ernet PHY to a

s most of the
as well as mos
ard includes an
ADC channels,

nd connect si
is, and on a
ctors on a side
ear regulator
nted verticall
thermally co
ve cooling m

t PHY’s. On t
an RJ45 conn

analog compo
st of the conne
n FPC connect
and the unbu

ignals with c
side cover. D
e cover via a
rs are mount
ly in the chas
onnects the
maintains the

the baseboar
nector. This p

31

onents,
ectors.
tor for
uffered

oaxial
Digital
DB44
ed on
ssis to
FPGA
FPGA

rd, we
roject

32

does not use USB or Ethernet ports. Also unused in this design are several multi‐gigabit (PCIe capable) transceivers on connector B, which have 4 reference clock input pairs, 8 receiver pairs and 8 transceiver pairs.

## Acknowledgements

We gratefully acknowledge many suggestions from Avrum Warshawsky, contributions of Lam Tran, helpful conversations with Marco Pomponio, and financial support from the National Science Foundation.

## References

1. Schussheim D, Gibble K. A many‐channel FPGA control system, Rev Sci Instrum. 2023; 94 085101 (2023). doi: 10.1063/5.0157330; arXiv:2307.16008
2. Leibrandt DR, Heidecker J. An open source digital servo for atomic, molecular, and optical physics experiments. Rev Sci Instrum. 2015; 86 123115. doi:10.1063/1.4938282
3. The power supply board design files are available at https://bit.ly/3LmEj9Y.
4. The MCFS design files are available online at https://github.com/ GibbleLab/FPGA.
5. FT81x Series Programmers Guide. Published online September 25, 2015. https://www.ftdichip.com/Support/Documents/ProgramGuides/FT81X_Series_Programmer_Guide. pdf
6. UG953: Vivado Design Suite 7 Series FPGA and Zynq‐7000 SoC Libraries Guide. Published online June 3, 2020. https://www.xilinx.com/support/documentation/sw_manuals/xilinx2019_1/ug953‐vivado‐ 7series‐libraries.pdf
7. UG471: 7 Series FPGAs SelectIO Resources. Published online May 8, 2018. https://www.xilinx.com/support/documentation/user_guides/ug471_7Series_SelectIO.pdf
8. PG261: System Integrated Logic Analyzer v1.1. Published online February 4, 2021. https://www.xilinx.com/content/dam/xilinx/support/documentation/ip_documentation/system_ila/v1_1/pg261‐system‐ila.pdf
9. Page 148 of [7].
10. UG908: Vivado Design Suite User Guide Programming and Debugging. Published online June 3, 2020. https://www.xilinx.com/support/documentation/sw_manuals/xilinx2020_1/ug908‐vivado‐ programming‐debugging.pdf
11. UG936: Vivado Design Suite Tutorial Programming and Debugging. Published online June 24, 2020. https://www.xilinx.com/support/documentation/sw_manuals/xilinx2020_1/ug936‐vivado‐tutorial‐ programming‐debugging.pdf

33

12. UG905: Vivado Design Suite User Guide Hierarchical Design. Published online June 3, 2020. https://www.xilinx.com/support/documentation/sw_manuals/xilinx2020_1/ug905‐vivado‐ hierarchical‐design.pdf
13. UG946: Vivado Design Suite Tutorial Hierarchical Design. Published online April 2, 2014. https://www.xilinx.com/support/documentation/sw_manuals/xilinx2014_1/ug946‐vivado‐ hierarchical‐design‐tutorial.pdf
14. i6AN Series: 75W, 9 to 40V Input Non‐Isolated DC‐DC Buck Converter with Negative Output. Accessed September 5, 2021. https://product.tdk.com/en/system/files?file=dam/doc/product/power/switching‐power/dc‐dc‐converter/catalog/i6an_e.pdf

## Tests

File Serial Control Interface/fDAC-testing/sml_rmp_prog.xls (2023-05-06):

f0 (Hz) | 10 | stepsize0 | 839 | (Number sent to FPGA) | Servo number | Path | Output file name
f1 | 20 | stepsize1 | 839 |  | 100 | C:\Users\Daniel\ | PIDparam.txt
f2 | 0.1 | stepsize2 | 8
f3 | 0.1 | stepsize3 | 8 | **Max stepsize is 2^16 = 65536
f4 | 10 | stepsize4 | 839 | **Dependent on frequency and amplitude
f5 | 0.1 | stepsize5 | 8 | **Stepsize is the number sent to the FPGA
f6 | 0.1 | stepsize6 | 8
f7 | 0.1 | stepsize7 | 8
f8 | 0.1 | stepsize8 | 8
f9 | 0.1 | stepsize9 | 8
f10 | 0.1 | stepsize10 | 8
f11 | 0.1 | stepsize11 | 8
f12 | 0.1 | stepsize12 | 8
f13 | 0.1 | stepsize13 | 8
offset0 (LSB) | 0
offset1 | 0
offset2 | 0
offset3 | 0
offset4 | 0
offset5 | 0
offset6 | 0
offset7 | 0
offset8 | 0
offset9 | 0
offset10 | 0
offset11 | 0
offset12 | 0
offset13 | 0
on0 | 3 | 2'b00 (0) = offset and ramp off, 2'b01 (1) = offset off ramp on, 2'b10 (2) = offset on ramp off, 2'b11 (3) = offset on ramp on.
on1 | 3
on2 | 3
on3 | 3
on4 | 3
on5 | 3
on6 | 3
on7 | 3
on8 | 3
on9 | 3
on10 | 3
on11 | 3
on12 | 3
on13 | 3
amp0 | 32000 | *Max is 2^15-1 = 32767
amp1 | 16000
amp2 | 32000
amp3 | 32000
amp4 | 32000
amp5 | 32000
amp6 | 32000
amp7 | 32000
amp8 | 32000
amp9 | 32000
amp10 | 32000
amp11 | 32000
amp12 | 32000
amp13 | 32000

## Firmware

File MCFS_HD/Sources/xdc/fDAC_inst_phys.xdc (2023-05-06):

####################################################################################
# Generated by Vivado 2020.1 built on 'Wed May 27 19:54:49 MDT 2020' by 'xbuild'
# Command Used: write_xdc -force -cell fDAC_inst ./Sources/xdc/fDAC_inst_phys.xdc
####################################################################################


####################################################################################
# Constraints from file : 'top_flpn.xdc'
####################################################################################

create_pblock pblock_fDAC_inst
add_cells_to_pblock [get_pblocks pblock_fDAC_inst] -top
resize_pblock [get_pblocks pblock_fDAC_inst] -add {SLICE_X8Y51:SLICE_X11Y249}
set_property CONTAIN_ROUTING 1 [get_pblocks pblock_fDAC_inst]
set_property IS_SOFT FALSE [get_pblocks pblock_fDAC_inst]
set_property PACKAGE_PIN F19 [get_ports fDACclkB_out]
set_property PACKAGE_PIN R17 [get_ports fDACclkC_out]
set_property IOSTANDARD LVCMOS33 [get_ports fDACclkB_out]
set_property IOSTANDARD LVCMOS33 [get_ports fDACclkC_out]
set_property PACKAGE_PIN E20 [get_ports fDAC0_sel]
set_property IOSTANDARD LVCMOS33 [get_ports fDAC0_sel]
set_property PACKAGE_PIN H17 [get_ports {fDAC0_out[15]}]
set_property PACKAGE_PIN H18 [get_ports {fDAC0_out[14]}]
set_property PACKAGE_PIN G19 [get_ports {fDAC0_out[13]}]
set_property PACKAGE_PIN F20 [get_ports {fDAC0_out[12]}]
set_property PACKAGE_PIN L19 [get_ports {fDAC0_out[11]}]
set_property PACKAGE_PIN L20 [get_ports {fDAC0_out[10]}]
set_property PACKAGE_PIN K20 [get_ports {fDAC0_out[9]}]
set_property PACKAGE_PIN J20 [get_ports {fDAC0_out[8]}]
set_property PACKAGE_PIN M17 [get_ports {fDAC0_out[7]}]
set_property PACKAGE_PIN L18 [get_ports {fDAC0_out[6]}]
set_property PACKAGE_PIN L17 [get_ports {fDAC0_out[5]}]
set_property PACKAGE_PIN K18 [get_ports {fDAC0_out[4]}]
set_property PACKAGE_PIN K16 [get_ports {fDAC0_out[3]}]
set_property PACKAGE_PIN K17 [get_ports {fDAC0_out[2]}]
set_property PACKAGE_PIN J18 [get_ports {fDAC0_out[1]}]
set_property PACKAGE_PIN J19 [get_ports {fDAC0_out[0]}]
set_property IOSTANDARD LVCMOS33 [get_ports {fDAC0_out[*]}]
set_property PACKAGE_PIN G11 [get_ports fDAC1_sel]
set_property IOSTANDARD LVCMOS33 [get_ports fDAC1_sel]
set_property PACKAGE_PIN F10 [get_ports {fDAC1_out[15]}]
set_property PACKAGE_PIN C14 [get_ports {fDAC1_out[14]}]
set_property PACKAGE_PIN C13 [get_ports {fDAC1_out[13]}]
set_property PACKAGE_PIN D14 [get_ports {fDAC1_out[12]}]
set_property PACKAGE_PIN D13 [get_ports {fDAC1_out[11]}]
set_property PACKAGE_PIN J13 [get_ports {fDAC1_out[10]}]
set_property PACKAGE_PIN H13 [get_ports {fDAC1_out[9]}]
set_property PACKAGE_PIN F14 [get_ports {fDAC1_out[8]}]
set_property PACKAGE_PIN F13 [get_ports {fDAC1_out[7]}]
set_property PACKAGE_PIN E13 [get_ports {fDAC1_out[6]}]
set_property PACKAGE_PIN E12 [get_ports {fDAC1_out[5]}]
set_property PACKAGE_PIN G12 [get_ports {fDAC1_out[4]}]
set_property PACKAGE_PIN F12 [get_ports {fDAC1_out[3]}]
set_property PACKAGE_PIN J11 [get_ports {fDAC1_out[2]}]
set_property PACKAGE_PIN J10 [get_ports {fDAC1_out[1]}]
set_property PACKAGE_PIN H12 [get_ports {fDAC1_out[0]}]
set_property IOSTANDARD LVCMOS33 [get_ports {fDAC1_out[*]}]
set_property PACKAGE_PIN H19 [get_ports fDAC2_sel]
set_property IOSTANDARD LVCMOS33 [get_ports fDAC2_sel]
set_property PACKAGE_PIN G20 [get_ports {fDAC2_out[15]}]
set_property PACKAGE_PIN D19 [get_ports {fDAC2_out[14]}]
set_property PACKAGE_PIN D20 [get_ports {fDAC2_out[13]}]
set_property PACKAGE_PIN G17 [get_ports {fDAC2_out[12]}]
set_property PACKAGE_PIN F18 [get_ports {fDAC2_out[11]}]
set_property PACKAGE_PIN C17 [get_ports {fDAC2_out[10]}]
set_property PACKAGE_PIN C18 [get_ports {fDAC2_out[9]}]
set_property PACKAGE_PIN C16 [get_ports {fDAC2_out[8]}]
set_property PACKAGE_PIN B16 [get_ports {fDAC2_out[7]}]
set_property PACKAGE_PIN B17 [get_ports {fDAC2_out[6]}]
set_property PACKAGE_PIN A17 [get_ports {fDAC2_out[5]}]
set_property PACKAGE_PIN E18 [get_ports {fDAC2_out[4]}]
set_property PACKAGE_PIN D18 [get_ports {fDAC2_out[3]}]
set_property PACKAGE_PIN C19 [get_ports {fDAC2_out[2]}]
set_property PACKAGE_PIN B19 [get_ports {fDAC2_out[1]}]
set_property PACKAGE_PIN A18 [get_ports {fDAC2_out[0]}]
set_property IOSTANDARD LVCMOS33 [get_ports {fDAC2_out[*]}]
set_property PACKAGE_PIN R16 [get_ports fDAC3_sel]
set_property IOSTANDARD LVCMOS33 [get_ports fDAC3_sel]
set_property PACKAGE_PIN M19 [get_ports {fDAC3_out[15]}]
set_property PACKAGE_PIN N18 [get_ports {fDAC3_out[14]}]
set_property PACKAGE_PIN H8 [get_ports {fDAC3_out[13]}]
set_property PACKAGE_PIN H9 [get_ports {fDAC3_out[12]}]
set_property PACKAGE_PIN F8 [get_ports {fDAC3_out[11]}]
set_property PACKAGE_PIN F9 [get_ports {fDAC3_out[10]}]
set_property PACKAGE_PIN D10 [get_ports {fDAC3_out[9]}]
set_property PACKAGE_PIN E10 [get_ports {fDAC3_out[8]}]
set_property PACKAGE_PIN D8 [get_ports {fDAC3_out[7]}]
set_property PACKAGE_PIN D9 [get_ports {fDAC3_out[6]}]
set_property PACKAGE_PIN B9 [get_ports {fDAC3_out[5]}]
set_property PACKAGE_PIN C9 [get_ports {fDAC3_out[4]}]
set_property PACKAGE_PIN A8 [get_ports {fDAC3_out[3]}]
set_property PACKAGE_PIN A9 [get_ports {fDAC3_out[2]}]
set_property PACKAGE_PIN J14 [get_ports {fDAC3_out[1]}]
set_property PACKAGE_PIN J8 [get_ports {fDAC3_out[0]}]
set_property IOSTANDARD LVCMOS33 [get_ports {fDAC3_out[*]}]
set_property PACKAGE_PIN U17 [get_ports fDAC4_sel]
set_property IOSTANDARD LVCMOS33 [get_ports fDAC4_sel]
set_property PACKAGE_PIN N17 [get_ports {fDAC4_out[15]}]
set_property PACKAGE_PIN P16 [get_ports {fDAC4_out[14]}]
set_property PACKAGE_PIN D16 [get_ports {fDAC4_out[13]}]
set_property PACKAGE_PIN D15 [get_ports {fDAC4_out[12]}]
set_property PACKAGE_PIN G16 [get_ports {fDAC4_out[11]}]
set_property PACKAGE_PIN H16 [get_ports {fDAC4_out[10]}]
set_property PACKAGE_PIN E16 [get_ports {fDAC4_out[9]}]
set_property PACKAGE_PIN E15 [get_ports {fDAC4_out[8]}]
set_property PACKAGE_PIN E17 [get_ports {fDAC4_out[7]}]
set_property PACKAGE_PIN F17 [get_ports {fDAC4_out[6]}]
set_property PACKAGE_PIN J16 [get_ports {fDAC4_out[5]}]
set_property PACKAGE_PIN J15 [get_ports {fDAC4_out[4]}]
set_property PACKAGE_PIN F15 [get_ports {fDAC4_out[3]}]
set_property PACKAGE_PIN G15 [get_ports {fDAC4_out[2]}]
set_property PACKAGE_PIN M16 [get_ports {fDAC4_out[1]}]
set_property PACKAGE_PIN K15 [get_ports {fDAC4_out[0]}]
set_property IOSTANDARD LVCMOS33 [get_ports {fDAC4_out[*]}]
set_property PACKAGE_PIN M21 [get_ports fDAC5_sel]
set_property IOSTANDARD LVCMOS33 [get_ports fDAC5_sel]
set_property PACKAGE_PIN P21 [get_ports {fDAC5_out[15]}]
set_property PACKAGE_PIN R21 [get_ports {fDAC5_out[14]}]
set_property PACKAGE_PIN P25 [get_ports {fDAC5_out[13]}]
set_property PACKAGE_PIN R25 [get_ports {fDAC5_out[12]}]
set_property PACKAGE_PIN R20 [get_ports {fDAC5_out[11]}]
set_property PACKAGE_PIN T20 [get_ports {fDAC5_out[10]}]
set_property PACKAGE_PIN U20 [get_ports {fDAC5_out[9]}]
set_property PACKAGE_PIN U19 [get_ports {fDAC5_out[8]}]
set_property PACKAGE_PIN T19 [get_ports {fDAC5_out[7]}]
set_property PACKAGE_PIN T18 [get_ports {fDAC5_out[6]}]
set_property PACKAGE_PIN M20 [get_ports {fDAC5_out[5]}]
set_property PACKAGE_PIN N19 [get_ports {fDAC5_out[4]}]
set_property PACKAGE_PIN T25 [get_ports {fDAC5_out[3]}]
set_property PACKAGE_PIN T24 [get_ports {fDAC5_out[2]}]
set_property PACKAGE_PIN N23 [get_ports {fDAC5_out[1]}]
set_property PACKAGE_PIN P23 [get_ports {fDAC5_out[0]}]
set_property IOSTANDARD LVCMOS33 [get_ports {fDAC5_out[*]}]
set_property PACKAGE_PIN L24 [get_ports fDAC6_sel]
set_property IOSTANDARD LVCMOS33 [get_ports fDAC6_sel]
set_property PACKAGE_PIN M24 [get_ports {fDAC6_out[15]}]
set_property PACKAGE_PIN N22 [get_ports {fDAC6_out[14]}]
set_property PACKAGE_PIN N21 [get_ports {fDAC6_out[13]}]
set_property PACKAGE_PIN K26 [get_ports {fDAC6_out[12]}]
set_property PACKAGE_PIN K25 [get_ports {fDAC6_out[11]}]
set_property PACKAGE_PIN T23 [get_ports {fDAC6_out[10]}]
set_property PACKAGE_PIN T22 [get_ports {fDAC6_out[9]}]
set_property PACKAGE_PIN P20 [get_ports {fDAC6_out[8]}]
set_property PACKAGE_PIN P19 [get_ports {fDAC6_out[7]}]
set_property PACKAGE_PIN N24 [get_ports {fDAC6_out[6]}]
set_property PACKAGE_PIN P24 [get_ports {fDAC6_out[5]}]
set_property PACKAGE_PIN R23 [get_ports {fDAC6_out[4]}]
set_property PACKAGE_PIN R22 [get_ports {fDAC6_out[3]}]
set_property PACKAGE_PIN P18 [get_ports {fDAC6_out[2]}]
set_property PACKAGE_PIN R18 [get_ports {fDAC6_out[1]}]
set_property PACKAGE_PIN T17 [get_ports {fDAC6_out[0]}]
set_property IOSTANDARD LVCMOS33 [get_ports {fDAC6_out[*]}]
create_generated_clock -name fDACclkB -source [get_pins ODDR_fDACclkB/C] -divide_by 1 [get_ports fDACclkB_out]
set_output_delay -clock [get_clocks fDACclkB] -max -0.600 [get_ports [list {fDAC0_out[1]} {fDAC0_out[2]} {fDAC0_out[3]} {fDAC0_out[4]} {fDAC0_out[5]} {fDAC0_out[6]} {fDAC0_out[7]} {fDAC0_out[8]} {fDAC0_out[9]} {fDAC0_out[10]} {fDAC0_out[11]} {fDAC0_out[12]} {fDAC0_out[13]} {fDAC0_out[14]} {fDAC0_out[15]} {fDAC0_out[0]}]]
set_output_delay -clock [get_clocks fDACclkB] -min -2.100 [get_ports [list {fDAC0_out[1]} {fDAC0_out[2]} {fDAC0_out[3]} {fDAC0_out[4]} {fDAC0_out[5]} {fDAC0_out[6]} {fDAC0_out[7]} {fDAC0_out[8]} {fDAC0_out[9]} {fDAC0_out[10]} {fDAC0_out[11]} {fDAC0_out[12]} {fDAC0_out[13]} {fDAC0_out[14]} {fDAC0_out[15]} {fDAC0_out[0]}]]
set_output_delay -clock [get_clocks fDACclkB] -max -0.600 [get_ports fDAC0_sel]
set_output_delay -clock [get_clocks fDACclkB] -min -2.100 [get_ports fDAC0_sel]
set_output_delay -clock [get_clocks fDACclkB] -max -0.600 [get_ports [list {fDAC1_out[1]} {fDAC1_out[2]} {fDAC1_out[3]} {fDAC1_out[4]} {fDAC1_out[5]} {fDAC1_out[6]} {fDAC1_out[7]} {fDAC1_out[8]} {fDAC1_out[9]} {fDAC1_out[10]} {fDAC1_out[11]} {fDAC1_out[12]} {fDAC1_out[13]} {fDAC1_out[14]} {fDAC1_out[15]} {fDAC1_out[0]}]]
set_output_delay -clock [get_clocks fDACclkB] -min -2.100 [get_ports [list {fDAC1_out[1]} {fDAC1_out[2]} {fDAC1_out[3]} {fDAC1_out[4]} {fDAC1_out[5]} {fDAC1_out[6]} {fDAC1_out[7]} {fDAC1_out[8]} {fDAC1_out[9]} {fDAC1_out[10]} {fDAC1_out[11]} {fDAC1_out[12]} {fDAC1_out[13]} {fDAC1_out[14]} {fDAC1_out[15]} {fDAC1_out[0]}]]
set_output_delay -clock [get_clocks fDACclkB] -max -0.600 [get_ports fDAC1_sel]
set_output_delay -clock [get_clocks fDACclkB] -min -2.100 [get_ports fDAC1_sel]
set_output_delay -clock [get_clocks fDACclkB] -max -0.600 [get_ports [list {fDAC2_out[1]} {fDAC2_out[2]} {fDAC2_out[3]} {fDAC2_out[4]} {fDAC2_out[5]} {fDAC2_out[6]} {fDAC2_out[7]} {fDAC2_out[8]} {fDAC2_out[9]} {fDAC2_out[10]} {fDAC2_out[11]} {fDAC2_out[12]} {fDAC2_out[13]} {fDAC2_out[14]} {fDAC2_out[15]} {fDAC2_out[0]}]]
set_output_delay -clock [get_clocks fDACclkB] -min -2.100 [get_ports [list {fDAC2_out[1]} {fDAC2_out[2]} {fDAC2_out[3]} {fDAC2_out[4]} {fDAC2_out[5]} {fDAC2_out[6]} {fDAC2_out[7]} {fDAC2_out[8]} {fDAC2_out[9]} {fDAC2_out[10]} {fDAC2_out[11]} {fDAC2_out[12]} {fDAC2_out[13]} {fDAC2_out[14]} {fDAC2_out[15]} {fDAC2_out[0]}]]
set_output_delay -clock [get_clocks fDACclkB] -max -0.600 [get_ports fDAC2_sel]
set_output_delay -clock [get_clocks fDACclkB] -min -2.100 [get_ports fDAC2_sel]
create_generated_clock -name fDACclkC -source [get_pins ODDR_fDACclkC/C] -divide_by 1 [get_ports fDACclkC_out]
set_output_delay -clock [get_clocks fDACclkC] -max -0.600 [get_ports [list {fDAC3_out[1]} {fDAC3_out[2]} {fDAC3_out[3]} {fDAC3_out[4]} {fDAC3_out[5]} {fDAC3_out[6]} {fDAC3_out[7]} {fDAC3_out[8]} {fDAC3_out[9]} {fDAC3_out[10]} {fDAC3_out[11]} {fDAC3_out[12]} {fDAC3_out[13]} {fDAC3_out[14]} {fDAC3_out[15]} {fDAC3_out[0]}]]
set_output_delay -clock [get_clocks fDACclkC] -min -2.100 [get_ports [list {fDAC3_out[1]} {fDAC3_out[2]} {fDAC3_out[3]} {fDAC3_out[4]} {fDAC3_out[5]} {fDAC3_out[6]} {fDAC3_out[7]} {fDAC3_out[8]} {fDAC3_out[9]} {fDAC3_out[10]} {fDAC3_out[11]} {fDAC3_out[12]} {fDAC3_out[13]} {fDAC3_out[14]} {fDAC3_out[15]} {fDAC3_out[0]}]]
set_output_delay -clock [get_clocks fDACclkC] -max -0.600 [get_ports fDAC3_sel]
set_output_delay -clock [get_clocks fDACclkC] -min -2.100 [get_ports fDAC3_sel]
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

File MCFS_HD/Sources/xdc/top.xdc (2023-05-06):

# Clocks
set_property PACKAGE_PIN AA4 [get_ports clk]

# Output LEDs on module board
set_property PACKAGE_PIN U9       [get_ports {led_out[3]}]
set_property IOSTANDARD  LVCMOS15 [get_ports {led_out[3]}]
set_property PACKAGE_PIN V12      [get_ports {led_out[2]}]
set_property IOSTANDARD  LVCMOS15 [get_ports {led_out[2]}]
set_property PACKAGE_PIN V13      [get_ports {led_out[1]}]
set_property IOSTANDARD  LVCMOS15 [get_ports {led_out[1]}]
set_property PACKAGE_PIN W13      [get_ports {led_out[0]}]
set_property IOSTANDARD  LVCMOS15 [get_ports {led_out[0]}]

# Shift-register serial lines
set_property PACKAGE_PIN E21      [get_ports SR_STROBE]
set_property IOSTANDARD  LVCMOS25 [get_ports SR_STROBE]
set_property PACKAGE_PIN D24      [get_ports SR_SCLK]
set_property IOSTANDARD  LVCMOS25 [get_ports SR_SCLK]
set_property PACKAGE_PIN E22      [get_ports SR_OUT]
set_property IOSTANDARD  LVCMOS25 [get_ports SR_OUT]
set_property PACKAGE_PIN D23      [get_ports SR_IN]
set_property IOSTANDARD  LVCMOS25 [get_ports SR_IN]
# Shift-register B serial lines
set_property PACKAGE_PIN C22      [get_ports SR_B_STROBE]
set_property IOSTANDARD  LVCMOS25 [get_ports SR_B_STROBE]
set_property PACKAGE_PIN D21      [get_ports SR_B_IN]
set_property IOSTANDARD  LVCMOS25 [get_ports SR_B_IN]
set_property PACKAGE_PIN N16      [get_ports SR_B_SCLK]
set_property IOSTANDARD  LVCMOS33 [get_ports SR_B_SCLK]

# Free digital lines
# Free digital lines (connector B)
set_property PACKAGE_PIN A19      [get_ports A19]
set_property IOSTANDARD  LVCMOS33 [get_ports A19]
set_property PACKAGE_PIN B14      [get_ports B14]
set_property IOSTANDARD  LVCMOS33 [get_ports B14]
set_property PACKAGE_PIN A14      [get_ports A14]
set_property IOSTANDARD  LVCMOS33 [get_ports A14]
set_property PACKAGE_PIN B15      [get_ports B15]
set_property IOSTANDARD  LVCMOS33 [get_ports B15]
set_property PACKAGE_PIN A15      [get_ports A15]
set_property IOSTANDARD  LVCMOS33 [get_ports A15]
set_property PACKAGE_PIN C12      [get_ports C12]
set_property IOSTANDARD  LVCMOS33 [get_ports C12]
# Free digital lines (connector C)
set_property PACKAGE_PIN U16      [get_ports U16]
set_property IOSTANDARD  LVCMOS33 [get_ports U16]
set_property PACKAGE_PIN M22      [get_ports M22]
set_property IOSTANDARD  LVCMOS33 [get_ports M22]
set_property PACKAGE_PIN R26      [get_ports R26]
set_property IOSTANDARD  LVCMOS33 [get_ports R26]
set_property PACKAGE_PIN P26      [get_ports P26]
set_property IOSTANDARD  LVCMOS33 [get_ports P26]
set_property PACKAGE_PIN N26      [get_ports N26]
set_property IOSTANDARD  LVCMOS33 [get_ports N26]
set_property PACKAGE_PIN M25      [get_ports M25]
set_property IOSTANDARD  LVCMOS33 [get_ports M25]
set_property PACKAGE_PIN L25      [get_ports L25]
set_property IOSTANDARD  LVCMOS33 [get_ports L25]
set_property PACKAGE_PIN M26      [get_ports M26]
set_property IOSTANDARD  LVCMOS33 [get_ports M26]
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

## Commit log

2023-05-06 Hierarchical Design Flow Project v1.0
2023-05-06 Baseboard files v1.0
    [BOM.xlsx, Connectors.SchDoc, LTC2194_0.SchDoc, LTC2194_1.SchDoc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]
2023-05-06 Power Supply v1.0
    [BOM.xlsx]
2023-05-06 Serial Control Interface v1.0
    [1083REF_PZT_Cav.xls, 361BBO_TempPID_125_1kHz.xls, 468_TempPID_125_1kHz.xls, 480_TempPID_125_1kHz.xls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]
